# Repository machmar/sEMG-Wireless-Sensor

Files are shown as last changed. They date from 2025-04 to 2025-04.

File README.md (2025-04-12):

# sEMG Wireless Sensor

This repository contains the code and hardware design files for a **wireless surface electromyography (sEMG) sensor**, developed as part of my Bachelor's thesis.

The device is designed to measure muscle activity using non-invasive surface electrodes and transmit the data wirelessly for real-time monitoring and analysis.

Its primary purpose is to assist during exercise by providing greater insight into individual muscle activation and strain.

---
<sub>This file was originally generated with the assistance of AI (ChatGPT) and subsequently reviewed and edited by a human.</sub>

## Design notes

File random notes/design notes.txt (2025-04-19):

any frequency higher then 2MHz on the spi clock on the sensor makes it not reliable and unable to send longer messages then 7 bytes, idk why,
hopefully it's just the bad PCB

something is up with the transmission still because in order to reliably transmit 25 bytes I have to send 26 bytes to the nrf chip
this error is consitent for 1MHz and 2MHz

also the app cannot handle 1kHz reliably so rn it's at 500Hz

It just DOES NOT reply to requests, but if it puts them into the fifo itself, it works just fine, I can't figure it out.

The flash start's massing up BAD at just 2MHz, I really don't know what's up with all that.

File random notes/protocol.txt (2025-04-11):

nrf interface:
Set send pipe address, set send data, send, read acks
Set get pipe address, select pipe to listen to, irq read data

protocol:
pipe 0 as fallback, otherwise always pipe 1
sensor always sends sEMG data, the first byte is the type, this is present for all transmists
PC part communicates by transmitting on the same pipe right after sending acks, again the first byte is the type, always
after sending data and getting acks, the device must wait at least as long as it took to send and receive acks to receive any commands.

types:
0x00: sEMG data (4 data bytes 2 diff, 2 reff), measured at 1kHz, when ack is not received, immeadiately store the transmited packet, and any subsequent, transmit on loop until you get a reply
0x01: battery level, responds in percentage
0x02: flash LED
0x03: lead status
0x04: new pipe request, if the accept is not received on the new pipe, fallback
0x05: new pipe accept (the device must store and verify the storage of new pipe before sending this)
0x06: measurement state data byte: 0x00 - stop, 0x01 - start 
0xfd: alive check
0xfe: go to permanent sleep
0xff: extended type, next byte is the type byte

pipes:
fallback  0x1122112233
pipe one  0x1122112201
pipe five 0x1122112205

if no acks are received for 30 seconds, go to fallback sending new pipe request with already set pipe

LEDs:
PC side: flash on serial receive, or data receive
sensor: orange solid on electrode removal, orange blink each n samples sent and acked, flash red on no ack in 30s, on flash LED blink both once

System services and errors:
(these are transmitted from the PC side to the vis app, they act as extended type messages to make it simple for decoding implementations,
unless othervise specified, all don't include any data bytes)
0xff 0x01: Booting after power on
0xff 0x02: Booting after reset command
0xff 0x03: Booting after UPDI reset
0xff 0x04: Booting after watchdog crash
0xff 0x05: Booting from an unknown reset state
0xff 0x06: Transmission error: ack not received
0xff 0x07: Transmission error: no response from local transmitter after 10s  (followed by a singla data byte that was received form the local transmitter)
0xff 0x08: Transmission error: message length set over 32 bytes
0xff 0x09: Transmission error: message length set less then 1 byte
0xff 0x0a: Controller state: Idle  
0xff 0x0b: Controller state: ReceptionWait  
0xff 0x0c: Controller state: ReceptionReady  
0xff 0x0d: Controller state: TransmissionStart  
0xff 0x0e: Controller state: TransmissionWait  
0xff 0x0f: Controller state: TransmissionConfirm  
0xff 0x10: Controller state: UnknownState

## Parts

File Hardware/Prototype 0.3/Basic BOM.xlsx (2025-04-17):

name | count | status | # | value | package
Sensor
R1, R2 | 2 | Ordered | 100 | 100R | 0402
R18 | 1 | Ordered | 20 | 47k | 0402
C11 | 1 | Missing |  | 270n | 0402
D1 | 1 | At home | 8 | Red | 0402
D2 | 1 | At home | 7 | Yellow | 0402
C7, C1 | 2 | At home | 8 | 10p | 0402
C8 | 1 | At home | 99 | 33n 10% | 0402
R3 | 1 | At home | 100 | 22k 1% | 0402
L1 | 1 | At home | 9 | 8n2H | 0402
L2 | 1 | At home | 9 | 2n7H | 0402
L3 | 1 | At home | 9 | 3n9H | 0402
C9 | 1 | Ordered | 20 | 1p5 0.1p | 0402 | only have 0.25pf tolerance
C10 | 1 | Ordered | 20 | 1p 0.1p | 0402
C18 | 1 | At home | 19 | 2n2 10% | 0402
C19 | 1 | At home | 19 | 4p7 0.25p | 0402
AntCap+ | 1 | Ordered | 20 | 5p1 0.05p | 0402
AntCap- | 1 | At home | 19 | 2p7 0.05p | 0402
X1 | 1 | At home | 4 | 16Mhz | --
R6, R5, R10, R11 | 4 | At home | 96 | 10M | 0402
R7, R8 | 2 | Ordered | 20 | 180k | 0402
R13 | 1 | Missing |  | 1M4 | 0402
R15, R14 | 2 | Missing |  | 44k | 0402
C17 | 1 | Ordered | 20 | 1n5 | 0402
C15, C13 | 2 | Ordered | 20 | 220n | 0402
C16 | 1 | Ordered | 20 | 22n | 0402
R16 | 1 | Ordered | 100 | 100k | 0402
R17 | 1 | Ordered | 100 | 1M | 0402
R9, R12 | 2 | Missing |  | 140k | 0402
C12 | 1 | Ordered | 20 | 1n | 0402
C2 | 1 | At home | 10 | 10u | 0402
C3, C4, C5, C6, C14, C21, C22 | 7 | Ordered | 100 | 100n | 0402
D | 1 | At home | 10 | DFN1006 | --
F1 | 1 | At home | 10 | 40mA | --
F2 | 1 | At home | 10 | PESD3V3 | --
BAT | 1 | At home | 7 | 2032 hldr | --
MEM | 1 | Missing |  | MXV25V80066 | USON8L | got some other to test
MCU | 1 | Missing |  | MSPM0G1107T | QFN24
COM | 1 | At home | 1 | NRF24L01+ | QFN20
AMP | 1 | Missing | 0 | AD8232 | QFN20
EMG1 | 1 | At home | 10 | steel wire | 0.35mm
Antenna | 1 | At home | 2 | Kyocera M310220 | --
name | count | status | # | value | package
Receiver
MCU | 1 | Ordered | 13 | attiny814 | SOIC14
R1 | 1 | At home | 80 | 100R | 0603
C1 | 1 | At home | 20 | 10u | 0603
C2, C3 | 2 | At home | 100 | 100n | 0603
LED1 | 1 | At home | 100 | Red | 3mm
R2 | 1 | At home | 100 | 10k | 0603 | (for reset pin to vcc)
UART | 1 | Ordered | 3 | FT232 | --
USB | 1 | At home | 5 | some micro (lazy) | --
LED2, LED3 | 2 | At home | 20 | red | 0603
R3, R4 | 2 | At home | 20 | 330R | 0603
FERR | 1 | Ordered | 10 | -- | 0603

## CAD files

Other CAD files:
Hardware/Prototype 0.1/Prototype 0.1.f3z
Hardware/Prototype 0.2/Prototype 0.2.f3z
Hardware/nrf to serial/nrf to serial.f3z

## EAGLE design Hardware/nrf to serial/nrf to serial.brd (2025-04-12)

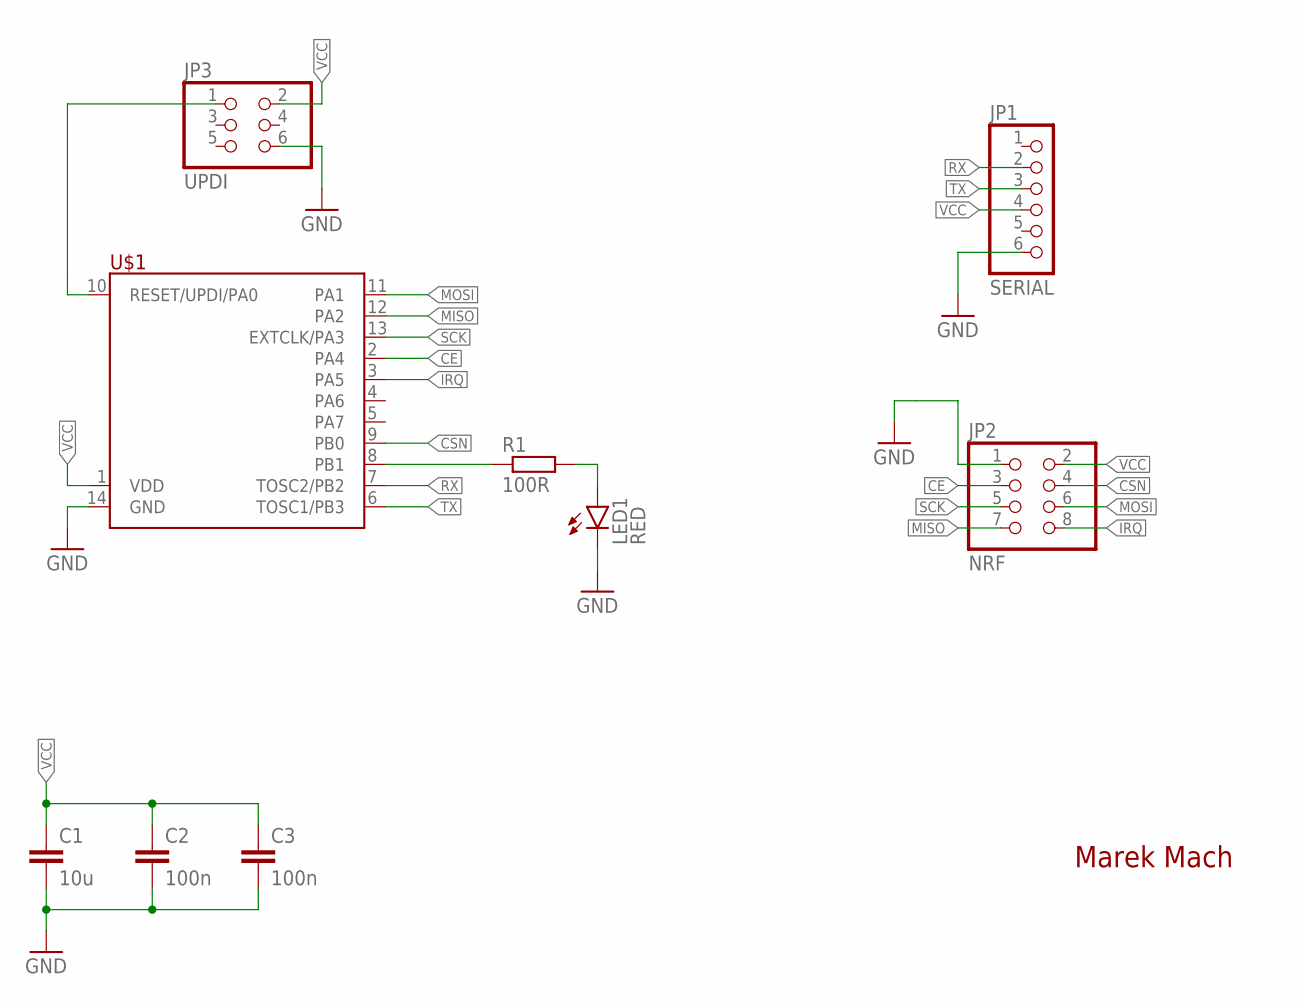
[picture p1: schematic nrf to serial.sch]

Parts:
C1: 10u; C0603
C2, C3: 100n; C0603
JP1: SERIAL; 1X06
JP2: NRF; 2X04
JP3: UPDI; 2X03
LED1: RED; LED3MM
R1: 100R; R0603
U$1: TINY214/414/814SOIC; SOIC14

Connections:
CE: JP2.3, U$1.2 (PA4)
CSN: JP2.4, U$1.9 (PB0)
GND: C1.2, C2.2, C3.2, JP1.6, JP2.1, JP3.6, LED1.K (C), U$1.14 (GND)
IRQ: JP2.8, U$1.3 (PA5)
MISO: JP2.7, U$1.12 (PA2)
MOSI: JP2.6, U$1.11 (PA1)
unnamed: R1.1, U$1.8 (PB1)
unnamed: JP3.1, U$1.10 (RESET/UPDI/PA0)
unnamed: LED1.A, R1.2
RX: JP1.2, U$1.7 (TOSC2/PB2)
SCK: JP2.5, U$1.13 (EXTCLK/PA3)
TX: JP1.3, U$1.6 (TOSC1/PB3)
VCC: C1.1, C2.1, C3.1, JP1.4, JP2.2, JP3.2, U$1.1 (VDD)

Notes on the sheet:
Marek Mach

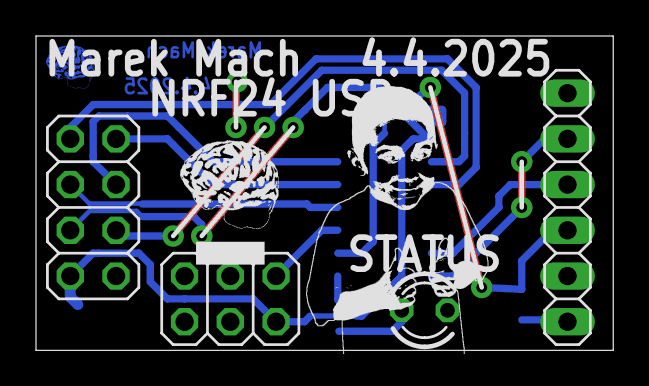
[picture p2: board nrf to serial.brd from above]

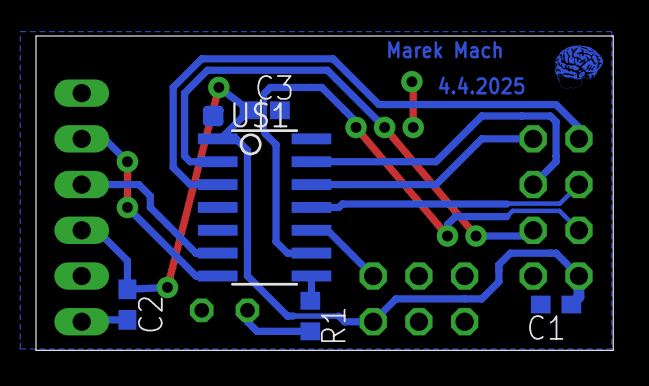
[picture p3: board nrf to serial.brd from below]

Board: 2 copper layers, 32.1 x 17.5 mm, 9 parts (5 on the bottom side), 13 nets.

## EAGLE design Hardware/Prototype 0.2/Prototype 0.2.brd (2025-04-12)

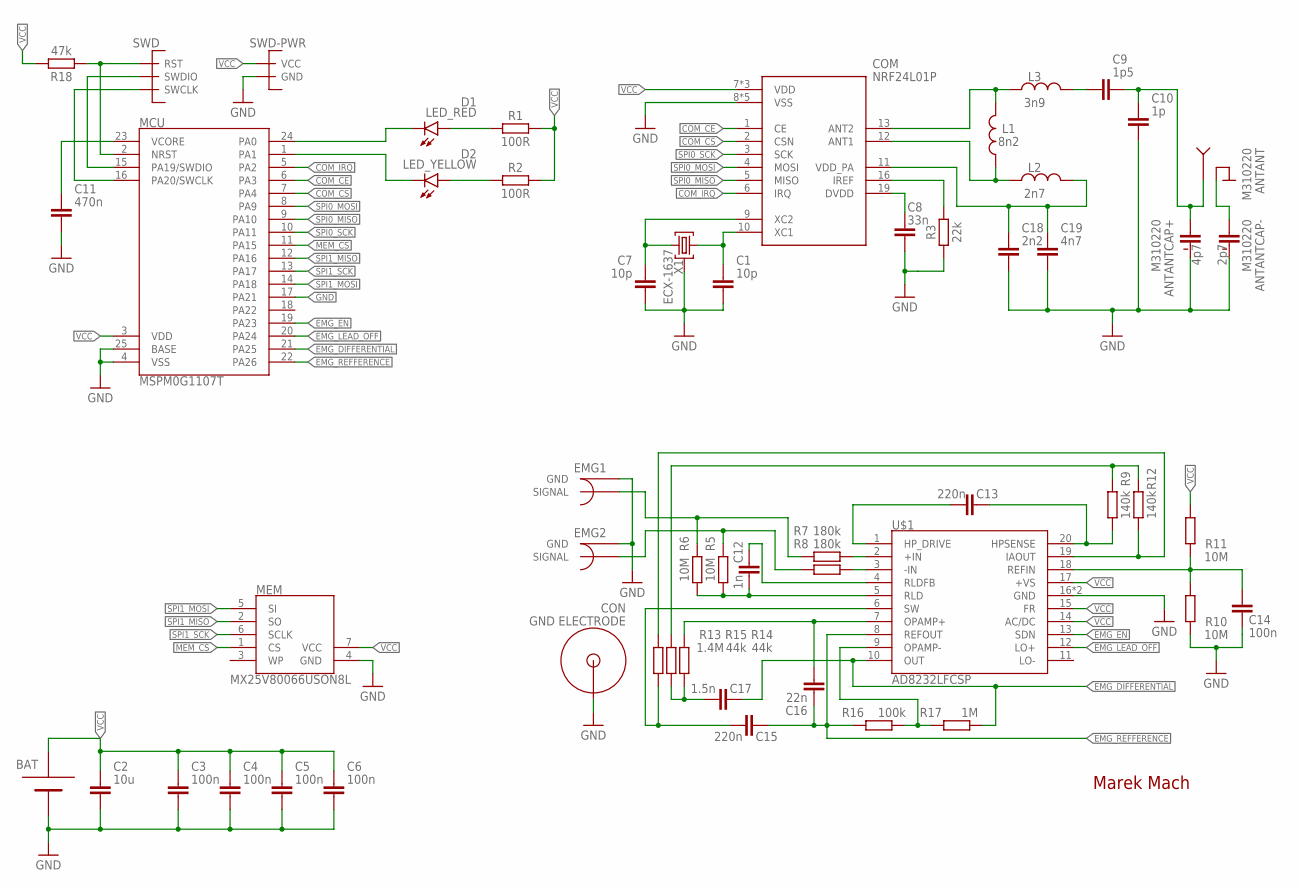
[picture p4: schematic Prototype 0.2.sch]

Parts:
ANT: M310220
BAT: 2025BAT-HLD-005-THM; BAT-HLD-005-THM
C1, C7: 10p; CAPC1005X60
C2: 10u; CAPC1608X85
C3, C4, C5, C6, C14: 100n; CAPC1608X85
C8: 33n; CAPC1005X60
C9: 1p5; CAPC1005X60
C10: 1p; CAPC1005X60
C11: 470n; CAPC1608X85
C12: 1n; CAPC1608X85
C13, C15: 220n; CAPC1608X85
C16: 22n; CAPC1608X85
C17: 1.5n; CAPC1608X85
C18: 2n2; CAPC1005X60
C19: 4n7; CAPC1005X60
COM: NRF24L01P; QFN50P400X400X100-21T265
CON: GND ELECTRODE; ELECTRODE_CONNECTOR
D1: LED_RED; LEDC1005X25N_FLAT-R
D2: LED_YELLOW; LEDC1005X25N_FLAT-Y
EMG1, EMG2: SHIELDED-CONNECTOR; SHIELDED-SMD
L1: 8n2; INDC1006X60N
L2: 2n7; INDC1006X60N
L3: 3n9; INDC1006X60N
MCU: MSPM0G1107T; QFN50P400X400X100-25T240
MEM: MX25V80066USON8L; SON50P300X200X50-8
R1, R2: 100R; RESC1608X60
R3: 22k; RESC1005X40
R5, R6, R10, R11: 10M; RESC1608X60
R7, R8: 180k; RESC1608X60
R9, R12: 140k; RESC1608X60
R13: 1.4M; RESC1608X60
R14, R15: 44k; RESC1608X60
R16: 100k; RESC1608X60
R17: 1M; RESC1608X60
R18: 47k; RESC1608X60
SWD: SWD; 3X
SWD-PWR: PWR; 2X
U$1: AD8232LFCSP; QFN50P400X400X80-21T275
X1: ECX-1637; WE-XTAL_IQXC-42

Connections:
COM_CE: COM.1 (CE), MCU.6 (PA3)
COM_CS: COM.2 (CSN), MCU.7 (PA4)
COM_IRQ: COM.6 (IRQ), MCU.5 (PA2)
EMG_DIFFERENTIAL: C17.2, MCU.21 (PA25), R17.1, U$1.10 (OUT)
EMG_EN: MCU.19 (PA23), U$1.13 (SDN)
EMG_LEAD_OFF: MCU.20 (PA24), U$1.12 (LO+)
EMG_REFFERENCE: C15.2, C16.1, MCU.22 (PA26), R16.2, U$1.8 (REFOUT)
GND: ANT.FEEDCAP-GND (NEG), ANT.GNDCAP-GND (NEG), BAT.P$1 (-), C1.2, C2.2, C3.2, C4.2, C5.2, C6.2, C7.2, C8.2, C10.2, C11.2, C14.1, C18.2, C19.2, COM.8 (VSS), COM.14 (VSS), COM.17 (VSS), COM.20 (VSS), COM.21 (VSS), CON.P$1, CON.P$2, CON.P$3, CON.P$4, EMG1.GND1 (GND), EMG1.GND2 (GND), EMG2.GND1 (GND), EMG2.GND2 (GND), MCU.4 (VSS), MCU.17 (PA21), MCU.25 (BASE), MEM.4 (GND), R3.1, R10.1, SWD-PWR.1 (GND), U$1.16 (GND), U$1.21 (GND), X1.2 (GND), X1.4 (GND)
MEM_CS: MCU.11 (PA15), MEM.1 (CS)
unnamed: C1.1, COM.10 (XC1), X1.1
unnamed: C11.1, MCU.23 (VCORE)
unnamed: D1.A, R1.1
unnamed: D2.A, R2.1
unnamed: C7.1, COM.9 (XC2), X1.3 (2)
unnamed: ANT.GNDCAP-GROUND (POS), ANT.GROUND
unnamed: C8.1, COM.19 (DVDD)
unnamed: COM.13 (ANT2), L1.2, L3.1
unnamed: C9.1, L3.2
unnamed: EMG1.SIG (SIGNAL), R6.2, R7.2
unnamed: EMG2.SIG (SIGNAL), R5.2, R8.2
unnamed: R7.1, U$1.2 (+IN)
unnamed: R8.1, U$1.3 (-IN)
unnamed: C16.2, R14.1, U$1.7 (OPAMP+)
unnamed: R16.1, R17.2, U$1.9 (OPAMP-)
unnamed: R9.2, R12.2, R15.2
unnamed: C12.1, R5.1, R6.1, U$1.5 (RLD)
unnamed: C13.1, U$1.1 (HP_DRIVE)
unnamed: C13.2, R9.1, U$1.20 (HPSENSE)
unnamed: COM.16 (IREF), R3.2
unnamed: C14.2, R10.2, R11.1, U$1.18 (REFIN)
unnamed: COM.12 (ANT1), L1.1, L2.1
unnamed: C15.1, R13.2, U$1.6 (SW)
unnamed: C17.1, R14.2, R15.1
unnamed: R12.1, R13.1, U$1.19 (IAOUT)
unnamed: C12.2, U$1.4 (RLDFB)
unnamed: ANT.FEED (ANTENNA), ANT.FEEDCAP-ANT (POS), C9.2, C10.1
unnamed: C18.1, C19.1, COM.11 (VDD_PA), L2.2
RED-STATUS-LED: D1.C, MCU.24 (PA0)
RST: MCU.2 (NRST), R18.1, SWD.1 (RST)
SPI0_MISO: COM.5 (MISO), MCU.9 (PA10)
SPI0_MOSI: COM.4 (MOSI), MCU.8 (PA9)
SPI0_SCK: COM.3 (SCK), MCU.10 (PA11)
SPI1_MISO: MCU.12 (PA16), MEM.2 (SO)
SPI1_MOSI: MCU.14 (PA18), MEM.5 (SI)
SPI1_SCK: MCU.13 (PA17), MEM.6 (SCLK)
SWCLK: MCU.16 (PA20/SWCLK), SWD.3 (SWCLK)
SWDIO: MCU.15 (PA19/SWDIO), SWD.2 (SWDIO)
VCC: BAT.P$2 (+), BAT.P$3 (+), C2.1, C3.1, C4.1, C5.1, C6.1, COM.7 (VDD), COM.15 (VDD), COM.18 (VDD), MCU.3 (VDD), MEM.7 (VCC), R1.2, R2.2, R11.2, R18.2, SWD-PWR.2 (VCC), U$1.14 (AC/DC), U$1.15 (FR), U$1.17 (+VS)
YELLOW-STATUS-LED: D2.C, MCU.1 (PA1)

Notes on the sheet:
Marek Mach
4p7
2p7

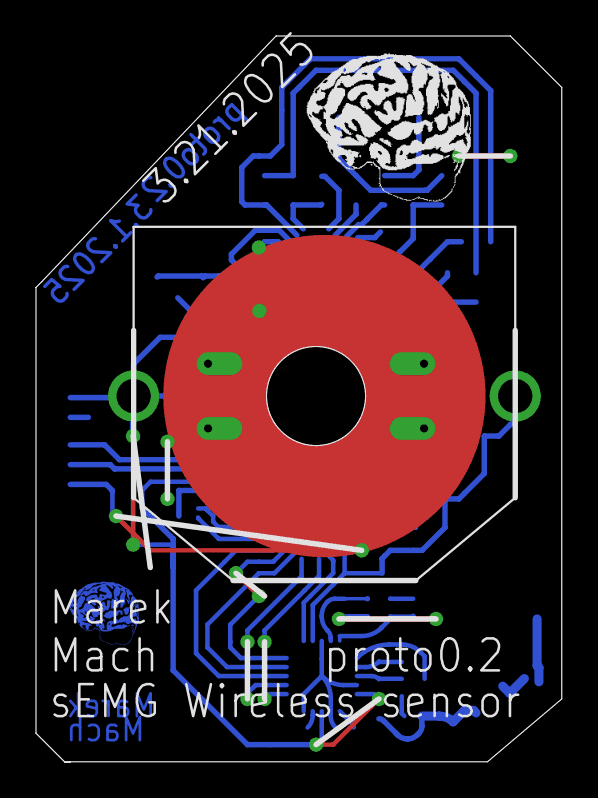
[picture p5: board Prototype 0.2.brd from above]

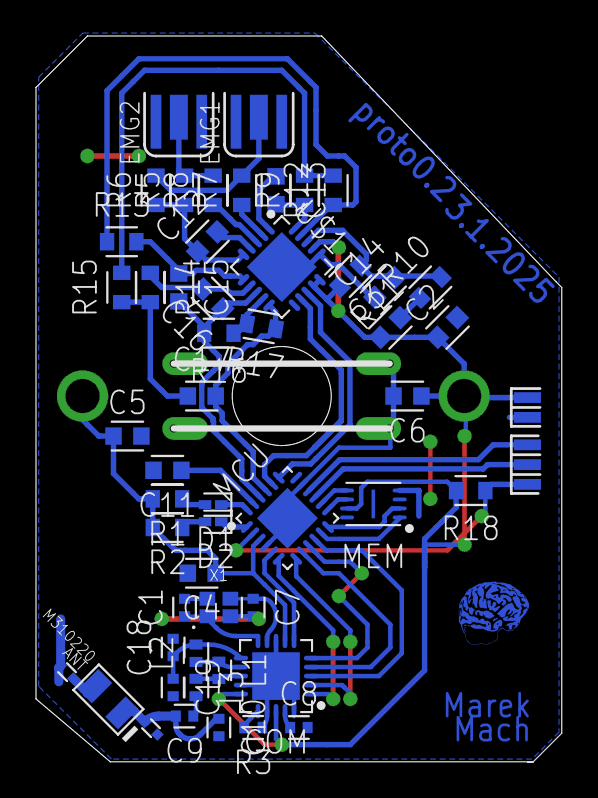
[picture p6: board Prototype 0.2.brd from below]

Board: 2 copper layers, 29.2 x 40.3 mm, 53 parts (52 on the bottom side), 49 nets.

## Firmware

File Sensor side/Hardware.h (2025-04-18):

#ifndef HARDWARE_H_
#define HARDWARE_H_

#include "ti/devices/msp/m0p/mspm0g110x.h"

#define HW_AMP_EN_SET (GPIOA->DOUTSET31_0 = 1 << 23)
#define HW_AMP_EN_CLR (GPIOA->DOUTCLR31_0 = 1 << 23)
#define HW_AMP_LEAD (GPIOA->DIN31_0 & 1 << 24)
#define HW_LED_RED_SET (GPIOA->DOUTSET31_0 = 1 << 0)
#define HW_LED_RED_CLR (GPIOA->DOUTCLR31_0 = 1 << 0)
#define HW_LED_RED_TGL (GPIOA->DOUTTGL31_0 = 1 << 0)
#define HW_LED_YEL_SET (GPIOA->DOUTSET31_0 = 1 << 1)
#define HW_LED_YEL_CLR (GPIOA->DOUTCLR31_0 = 1 << 1)
#define HW_LED_YEL_TGL (GPIOA->DOUTTGL31_0 = 1 << 1)
#define HW_ADC_BAT (ADC0->ULLMEM.MEMRES[0])
#define HW_ADC_REF (ADC0->ULLMEM.MEMRES[2])
#define HW_ADC_EMG (ADC0->ULLMEM.MEMRES[1])
#define HW_NRF_CS_SET (GPIOA->DOUTSET31_0 = 1 << 4)
#define HW_NRF_CS_CLR (GPIOA->DOUTCLR31_0 = 1 << 4)
#define HW_NRF_CE_SET (GPIOA->DOUTSET31_0 = 1 << 3)
#define HW_NRF_CE_CLR (GPIOA->DOUTCLR31_0 = 1 << 3)
#define HW_FLASH_CS_SET (GPIOA->DOUTSET31_0 = 1 << 15)
#define HW_FLASH_CS_CLR (GPIOA->DOUTCLR31_0 = 1 << 15)

#endif

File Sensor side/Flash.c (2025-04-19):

#include "Flash.h"
#include "FlashRegs.h"
#include "Hardware.h"
#include "ti/driverlib/dl_spi.h"
#include "ti/driverlib/m0p/dl_core.h"

#define SPI_WAIT_TRANSFER_COMPLETE while(SPI1->STAT & SPI_STAT_BUSY_MASK)
#define SPI_WAIT_FIFO_NOT_FULL while(~SPI1->STAT & (1 << SPI_STAT_TFE_MASK))
#define SPI_DATA(x) SPI_WAIT_FIFO_NOT_FULL; SPI1->TXDATA = (x)

uint32_t volatile spi_got_back_[10];
uint32_t volatile got_back_len_;
uint8_t *receive_data_;
uint32_t receive_data_size_; ///<Mostly a safety check, shouldn't ever be needed anyway.
uint32_t volatile save_locally_; ///< After this number of bytes start saving to provided buffer

FlashState_t Flash_Init() {
    for (uint32_t i = 0; i < 10; i++) spi_got_back_[i] = 0;
    got_back_len_ = 0;
    receive_data_ = 0; // NULL isn't recognised for some reason
    receive_data_size_ = 0;
    save_locally_ = 0;

    // check manufacturer ID
    HW_FLASH_CS_CLR;
    SPI_DATA(F_REG_RDID);
    SPI_DATA(0x00); // manufacturer ID
    SPI_WAIT_TRANSFER_COMPLETE;
    if (spi_got_back_[1] == 0xff || spi_got_back_[1] == 0x00) {
        return StateFlash_NotResponding;
    }

    return StateFlash_Idle;
}

FlashState_t Flash_Read(uint8_t *data, uint32_t address, uint32_t count) {
    FlashState_t tmp = Flash_GetState();
    if (tmp != StateFlash_Idle && tmp != StateFlash_Locked) return tmp; // check if it's in idle

    // save the needed variables
    save_locally_ = 4;
    receive_data_size_ = count;
    receive_data_ = data;

    HW_FLASH_CS_CLR;
    SPI_DATA(F_REG_READ);
    SPI_DATA((address & 0x00ff0000) >> 16);
    SPI_DATA((address & 0x0000ff00) >> 8);
    SPI_DATA((address & 0x000000ff) >> 0);
    for (uint32_t i = 0; i < count; i++) {
        SPI_DATA(0x00); // reading bytes out from the memory
    }
    SPI_WAIT_TRANSFER_COMPLETE;

    return Flash_GetState();
}

FlashState_t Flash_Write(uint8_t *data, uint32_t address, uint32_t count) {
    FlashState_t tmp = Flash_GetState();
    if (tmp != StateFlash_Idle) return tmp; // check if it's in idle

    
    for (uint32_t i = 0; i < 8; i++) { // try to set the bit 8 times
        // enable write
        HW_FLASH_CS_CLR;
        SPI_DATA(F_REG_WREN);
        SPI_WAIT_TRANSFER_COMPLETE;

        // check if write is enabled
        HW_FLASH_CS_CLR;
        SPI_DATA(F_REG_RDSR);
        SPI_DATA(0x00);
        SPI_WAIT_TRANSFER_COMPLETE;
        if (spi_got_back_[1] & (1 << 1)) goto exitWriteEnableLoop; // using goto just to be sure

        if (i == 7) return Flash_GetState();
    }
    exitWriteEnableLoop:

    // write reg and address
    save_locally_ = 0; // it stops saving after the 10 byte limit is reached (we don't care about the data)
    HW_FLASH_CS_CLR;
    SPI_DATA(F_REG_PP);
    SPI_DATA((address & 0x00ff0000) >> 16);
    SPI_DATA((address & 0x0000ff00) >> 8);
    SPI_DATA((address & 0x000000ff) >> 0);
    for (uint32_t i = 0; i < count && i < 256; i++) {
        SPI_DATA(data[i]); // writing a byte to the memory
    }
    SPI_WAIT_TRANSFER_COMPLETE;

    return Flash_GetState();
}

FlashState_t Flash_Lock() { // not implemented (don't care)
    return StateFlash_NotResponding;
}

FlashState_t Flash_Unlock() { // not implemented (don't care)
    return StateFlash_NotResponding;
}

FlashState_t Flash_GetState() {
    HW_FLASH_CS_CLR;
    SPI_DATA(F_REG_RDSR);
    SPI_DATA(0x00);
    SPI_WAIT_TRANSFER_COMPLETE;
    if (spi_got_back_[1] & (1 << 0)) return StateFlash_Writing;
    else if (spi_got_back_[1] & (0b1111 << 2)) return StateFlash_Locked;
    else if (spi_got_back_[1] != 0x00 && spi_got_back_[1] != 0xff) return StateFlash_Idle;
    else {
        // check manufacturer ID
        HW_FLASH_CS_CLR;
        SPI_DATA(F_REG_RDID);
        SPI_DATA(0x00); // manufacturer ID
        SPI_WAIT_TRANSFER_COMPLETE;
        if (spi_got_back_[1] == 0xff || spi_got_back_[1] == 0x00) {
            return StateFlash_NotResponding;
        }
    }
    return StateFlash_Idle;
}

void Flash_SPIHandler() {
    static uint32_t receive_pos = 0;

    switch(SPI1->CPU_INT.IIDX) {
    case DL_SPI_IIDX_RX_FULL:
        // save externally if it's requested, or locally
        while ((~SPI1->STAT & SPI_STAT_RFE_EMPTY) && (receive_pos < UINT32_MAX)) {
            if (receive_pos >= save_locally_ && save_locally_ > 0) {
                // prevent going out of the array and null dereference
                if (((receive_pos - save_locally_) < receive_data_size_) && receive_data_ != 0) {
                    receive_data_[receive_pos - save_locally_] = SPI1->RXDATA;
                }
            }
            else  {
                if (receive_pos < 10) {
                    spi_got_back_[receive_pos] = SPI1->RXDATA;
                }
                else {
                    uint8_t dont_care = SPI1->RXDATA; // have to read from the RX fifo to exit this interrupt loop
                }
            }
            receive_pos++;
        }
        break;

    case DL_SPI_IIDX_IDLE:
        HW_FLASH_CS_SET;
        // save externally if it's requested, or locally
        while ((~SPI1->STAT & SPI_STAT_RFE_EMPTY) && (receive_pos < UINT32_MAX)) {
            if (receive_pos >= save_locally_ && save_locally_ > 0) {
                // prevent going out of the array and null dereference
                if (((receive_pos - save_locally_) < receive_data_size_) && receive_data_ != 0) {
                    receive_data_[receive_pos - save_locally_] = SPI1->RXDATA;
                }
            }
            else  {
                if (receive_pos < 10) {
                    spi_got_back_[receive_pos] = SPI1->RXDATA;
                }
                else {
                    uint8_t dont_care = SPI1->RXDATA; // have to read from the RX fifo to exit this interrupt loop
                }
            }
            receive_pos++;
        }

        got_back_len_ = receive_pos;
        receive_pos = 0;
        receive_data_ = 0;
        receive_data_size_ = 0;
        save_locally_ = 0;
        break;
    }
}

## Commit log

2025-04-06 make sensorSide folder
2025-04-09 Adding data transmission (to sensor)
2025-04-09 I forgot to commit for the entire day 💀
2025-04-10 Added millis
2025-04-11 correct sending to sensor
2025-04-11 transmits 5 samples at a time
    total transfer @500Hz now
2025-04-11 automatically send electrode state
2025-04-12 added hardware design files
    [Prototype 0.1.brd, Prototype 0.1.f3z, Prototype 0.2.brd, Prototype 0.2.f3z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]
2025-04-17 added a simple BOM
    [Basic BOM.xlsx]
